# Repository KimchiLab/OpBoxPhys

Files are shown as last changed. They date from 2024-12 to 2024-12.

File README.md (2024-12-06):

# OpBox System for Physiology & Camera Recordings

Physiology acquisition (EEG & EMG) using the **OpBox System**  
(Open Source/Operant Boxes for Behavioral Neurophysiology)
 
Reproducible in vivo electrophysiology experiments require the collection of data from multiple subjects, often for extended periods. Studying multiple subjects for extended periods can be made more efficient through simultaneous recordings, but scaling up recordings to accommodate larger numbers of subjects simultaneously requires coordination and consideration of costs and flexibility. To facilitate this process, we have developed OpBox, an open source set of tools to acquire electroencephalography (EEG) and electromyography (EMG) flexibly from multiple rodent subjects simultaneously. OpBox combines open source hardware and software with off-the-shelf components to create a system that is inexpensive on a per-subject basis and can be easily deployed for multiple subjects. Coded in MATLAB, software widely used in neuroscience laboratories, OpBox scripts can simultaneously collect and display real-time EEG and EMG, and can be integrated with other data streams such as behavior. OpBox also calculates and displays real-time spectral representations and event-related potentials (ERPs). To verify the performance of our system, we compare our amplifiers with two other commercial amplifiers using common benchmarks. We also demonstrate that our acquisition system can reliably record multi-channel data from multiple subjects, and has been successfully tested with at least 12 subjects running simultaneously on a single standard desktop computer. Together, OpBox increases the flexibility and lowers the cost for simultaneous acquisition of electrophysiology data from multiple subjects.

## Folders
* **Amplifier PCB Designs**: Multi-channel, open source OpBox amplifier PCB designs (3 and 4 channel)
* **How to Build and Parts List**: How to build information and parts lists for OpBox amplifiers
* **OpBox Phys Scripts**: MATLAB based scripts to acquire data from OpBox amplifiers, using National Instruments data acquisition devices

## Changing Windows USB Webcam names
* Note, this requires editing the Registry, which should only be undertaken by experienced users at their own risk after backing it up *  
1. Open Device Manager
1. Right click on the camera, select Properties
1. Click on the details tab
1. Under Property, select Driver Key
1. Right click and copy the Value
1. Run regedit.exe
1. Go to HKEY_LOCAL_MACHINE -> SYSTEM -> ControlSet001 (left click on that)
1. Ctrl-F to find: paste the Driver Key Value
1. It should take you to a folder within Enum -> USB
1. Double Click on Friendly Name and adjust the name (e.g. HD USB Camera -> HD USB Camera 01)
1. Back to Device Manager, under Property, select Device instance path
1. Right click and copy the Value
1. Back to Registry Editor
1. Go to HKEY_LOCAL_MACHINE -> SYSTEM -> CurrentControlSet
1. Ctrl-F to find: paste the Device instanc path Value
1. It should take you to a folder within Control -> DeviceClasses
1. Go within that folder to #GLOBAL -> Device Parameters
1. Double Click on Friendly Name and adjust the name (e.g. HD USB Camera -> HD USB Camera 01)
1. Back to Device Manager -> Action -> Scan for Hardware Changes
1. You may need to restart Matlab or at least run imaqreset, which will cause problems if OpBox is running, so stop all recordings first

## FYI: Pinnacle 2 EEG/ 1 EMG Connections

| Mouse Connection | Pinnacle Connector | Pinnacle Label | Plastics1 Cable Color | Plug Pos | Commutator Socket Pos | Commutator color | Amp Channel | BNC Channel | Matlab Color | Desc |
| --- | --- | --- | --- | --- | --- | --- | --- | --- | --- | --- |
| EEG Ant Left | Ant Left | AGND | Red | 4 | 6 | ***Black*** | G | | | |
| EEG Ant Right | Ant Mid | EEG2 | White | 5 | 5 | White | EEG B | 2 | Orange | Contra-A/P|
| EMG Right | Ant Right | EMG B | Black | 6 | 4 | ***Red*** | EMG | | | |
| EEG Post Left | Post Left | EEG Common | Green | 1 | 1 | Green | EEG Ref | | | |
| EEG Post Right | Post Mid | EEG1 | Blue | 2 | 2 | Blue | EEG A | 1 | Blue | Contra-Horiz |
| EMG Left | Post Right | EMG A | Yellow | 3 | 3 | Yellow | EMG | 3 | Yellow | EMG |

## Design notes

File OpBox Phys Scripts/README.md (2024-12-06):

# OpBox Phys

Physiology acquisition (EEG & EMG) using the **OpBox System**  
(Open Source/Operant Boxes for Behavioral Neurophysiology)
 
The OpBox Phys software library was written in MATLAB to use National Instruments Data Acquisition Devices to collect physiology and behavioral data from multiple subjects simultaneously. It requires MATLAB's Data Acquisition Toolbox (R2020a or newer) and NI's DAQmx drivers.

## Scripts/Functions
OpBox MATLAB scripts are grouped into several types:  

* OpBox_\*.m: Intended to be called by users  
* OpBoxPhys_\*.m: Called internally by other scripts
* \*.csv: Spreadsheets (in text based comma separated value format) used for configuration by users

## Main Functions
* *OpBox_Setup*: Setup data acquisition devices
* *OpBox_Add*: Add subjects once the system has been setup
* *OpBox_Remove*: Remove one or more subjects that are currently being recorded from
* *OpBox_Stop*: Stop data acquisition

## Additional functions
* *OpBox\_Axis\_Time*: Change the axis for the display of temporal data
* *OpBox_ResetEP*: Reset the evoked potentials being displayed
* *OpBox_LoadPhysData*: Load data collected in a prior session
	* data = OpBox_LoadPhysData(fullfile(server_dir_name, filename_bin)); % where filename_bin = the name of a binary .bin opbox file

## Configuration
The .csv spreadsheets can be edited using a text editor or standard spreadsheet program. If using a program such as Excel, make sure to save in the same text based .csv format when done

* *InfoBoxes.csv*: Configuration for various the various "OpBoxes". This includes assignments of different DAQ devices and input channels (analog, digital, rotary encoders) to specific boxes/amplifiers. It is also possible to associate webcams.
* *InfoSubjects.csv*: Configuration for assigments of various subjects to various boxes and groups

Webcams can be used to monitor and save video during acquisition, although MATLAB's image acquisition from webcams can be slower than other more dedicated systems. OpBox will try to connect to webcams using MATLAB's winvideo driver. In general OpBox has been written for Windows, but can be adapted to other OSes.

## Acknowledgements

This library includes the file [csvimport.m](http://uk.mathworks.com/matlabcentral/fileexchange/23573-csvimport) in OpBoxPhys_InfoBoxSubj.m
This file is used to load csv files for OpBox in MATLAB R2013a. 
Subsequent MATLAB releases included the function *readtable.m*

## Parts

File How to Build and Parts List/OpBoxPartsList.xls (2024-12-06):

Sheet: OpBox
Ordering frequency | SystemPart | Equipment | Vendor | Cost | # | Total | VendorPart | MfgPart | Manufacturer | Web | Notes | Cost per OpBox | $269.59 | Possible 1 time expenses | $1560.36
For 10 OpBoxes | Physiology: Acquisition from Amplifier | 10' BNC M-M Patch Cable RG58 Coax 50 ohm | M C M Electronics | 3.7700 | 8 | $30.16 | 24-15626 | 24-15626 | Pro Signal | http://www.mcmelectronics.com/product/24-15626 | Connection from Physiology Amplifier to Acquisition
For 10 OpBoxes | Physiology: Battery Power | Battery Holder 2xaa Snap 150mm Lead | M C M Electronics | 0.4100 | 20 | $8.20 | 28-12561 | 23VB21A | Pro Signal | http://www.mcmelectronics.com/product/PRO-POWER-23VB21A-/28-12561 | Battery Holder (2 AA)
For 10 OpBoxes | Physiology: Amplifier | BUMPER CYLIN 0.312" DIA BLK | Digi-Key | 0.0762 | 144 | $10.97 | SJ5746-0-ND | SJ61A1 | 3M | http://www.digikey.com/product-detail/en/SJ61A1/SJ5746-0-ND/1768456 | Rubber bumper feet for amp
For 10 OpBoxes | Physiology: Cable | Cables: 6 Channel Open ended: Spring: 100cm long | Plastics1 | 32.7000 | 10 | $327.00 | 363-000 W/ SPRING |  |  | http://www.plastics1.com/Gallery-PRC.php?CMD=VIEW | Cables: 6 channels with Spring shielding
For 10 OpBoxes: 4Ch | Physiology: Amplifier 4Ch | CAP CER 0.047UF 50V 5% RADIAL | Digi-Key | 0.4600 | 40 | $18.40 | 445-8327-ND | FK16C0G1H473J | TDK Corporation | http://www.digikey.com/product-detail/en/FK16C0G1H473J/445-8327-ND/2815257 | For 2 pole Active Low pass filter, Gain = 1, F = 200 Hz, Q~0.71
For 10 OpBoxes: 3Ch | Physiology: Amplifier 3Ch | CAP CER 0.047UF 50V 5% RADIAL | Digi-Key | 0.4670 | 30 | $14.01 | 445-8327-ND | FK16C0G1H473J | TDK Corporation | http://www.digikey.com/product-detail/en/FK16C0G1H473J/445-8327-ND/2815257 | For 2 pole Active Low pass filter, Gain = 1, F = 200 Hz, Q~0.71
For 10 OpBoxes: 4Ch | Physiology: Amplifier 4Ch | CAP CER 0.1UF 50V 5% RADIAL | Digi-Key | 0.4001 | 280 | $112.03 | 445-8325-ND | FK16C0G1H104J | TDK Corporation | http://www.digikey.com/product-detail/en/FK16C0G1H104J/445-8325-ND/2815255 | For power inputs & 2 pole Active Low pass filter, Gain = 1, F = 200 Hz, Q~0.71. COG 5%
For 10 OpBoxes: 3Ch | Physiology: Amplifier 3Ch | CAP CER 0.1UF 50V 5% RADIAL | Digi-Key | 0.4000 | 210 | $84.00 | 445-8325-ND | FK16C0G1H104J | TDK Corporation | http://www.digikey.com/product-detail/en/FK16C0G1H104J/445-8325-ND/2815255 | For power inputs & 2 pole Active Low pass filter, Gain = 1, F = 200 Hz, Q~0.71. COG 5%
For 10 OpBoxes: 4Ch | Physiology: Amplifier 4Ch | CAP FILM 1UF 63VDC RADIAL | Digi-Key | 0.3120 | 100 | $31.20 | 495-1119-ND | B32529C105J | EPCOS Inc | http://www.digikey.com/product-detail/en/B32529C105J/495-1119-ND/592697 | For 2 pole Active High pass filter, Gain = 1, F = 0.28 Hz, Q~0.71. Film Cap
For 10 OpBoxes: 3Ch | Physiology: Amplifier 3Ch | CAP FILM 1UF 63VDC RADIAL | Digi-Key | 0.4550 | 60 | $27.30 | 495-1119-ND | B32529C105J | EPCOS Inc | http://www.digikey.com/product-detail/en/B32529C105J/495-1119-ND/592697 | For 2 pole Active High pass filter, Gain = 1, F = 0.28 Hz, Q~0.71. Film Cap
For 10 OpBoxes: 3Ch | Physiology: Amplifier 3Ch | CONN BNC JACK R/A 50 OHM PCB | Digi-Key | 1.7252 | 30 | $51.76 | A97553-ND | 1-1337543-0 | TE Connectivity | http://www.digikey.com/product-detail/en/1-1337543-0/A97553-ND/1755940 | BNC output jacks
For 10 OpBoxes: 3Ch | Physiology: Amplifier 3Ch | CONN HEADER VERT .100 2POS 30AU | Digi-Key | 0.7300 | 20 | $14.60 | A28473-ND | 103908-1 | TE Connectivity | http://www.digikey.com/product-detail/en/103908-1/A28473-ND/298654 | AmpModu 2 pin male pins w/housing for amp power input, with Latch. Press-Fit, Solder
For 10 OpBoxes: 4Ch | Physiology: Amplifier 4Ch | CONN HEADER VERT .100 2POS 30AU | Digi-Key | 0.6610 | 20 | $13.22 | A28473-ND | 103908-1 | TE Connectivity | http://www.digikey.com/product-detail/en/103908-1/A28473-ND/298654 | AmpModu 2 pin male pins w/housing for amp power input, with Latch. Press-Fit, Solder
For 10 OpBoxes: 4Ch | Physiology: Amplifier 4Ch | CONN MOD JACK 8P8C | Digi-Key | 4.7690 | 10 | $47.69 | 380-1100-ND | SS-82000-002 |  | http://www.digikey.com/product-detail/en/SS-82000-002/380-1100-ND/459026 | "Ethernet" Input for NI system
For 10 OpBoxes: 4Ch | Physiology: Amplifier 4Ch | CONN MOD JACK R/A 8P8C SHIELDED | Digi-Key | 1.6240 | 10 | $16.24 | 380-1047-ND | SS-7188S-A-NF | Stewart Connector | http://www.digikey.com/product-detail/en/SS-7188S-A-NF/380-1047-ND/388309 | "Ethernet" Output for Amp 4Ch
For 10 OpBoxes | Physiology: Commutator | CONN PIN CONT 26-30AWG GOLD | Digi-Key | 0.0948 | 60 | $5.69 | 1-794613-1-ND | 1-794613-1 | TE Connectivity | http://www.digikey.com/product-detail/en/1-794613-1/1-794613-1-ND/2259374 | Commutator male pins: Mico MATE-N-LOCK, AMP. Male pin contacts. 3mm TE connectors
For 10 OpBoxes | Physiology: Commutator | CONN PLUG 3MM 6POS DL MATE-N-LOK | Digi-Key | 0.6090 | 10 | $6.09 | A30271-ND | 794616-6 | TE Connectivity | http://www.digikey.com/product-detail/en/794616-6/A30271-ND/684994 | Commutator plug: Mico MATE-N-LOCK, AMP. Male pin holder. 3mm TE connectors
For 10 OpBoxes | Physiology: Cable | CONN RCPT 3MM 6POS DL MATE-N-L | Digi-Key | 0.4900 | 10 | $4.90 | A30295-ND | 794617-6 | TE Connectivity | http://www.digikey.com/product-detail/en/794617-6/A30295-ND/685018 | Crimp connectors for male/female pin combo for commutator: Mico MATE-N-LOCK, AMP. Female socket holder
For 10 OpBoxes | Physiology: Battery Power | CONN RECPT 2POS .1" POL UNLOAD | Digi-Key | 0.3570 | 20 | $7.14 | A28393-ND | 104257-1 | TE Connectivity | http://www.digikey.com/product-detail/en/104257-1/A28393-ND/289301 | AmpModu 2 pin housing for female sockets for battery power output, with Latch
For 10 OpBoxes | Physiology: Battery Power | CONN SOCKET 22-26AWG 30AU CRIMP | Digi-Key | 0.1776 | 40 | $7.10 | A32513-ND | 1-104480-6 | TE Connectivity | http://www.digikey.com/product-detail/en/1-104480-6/A32513-ND/1014904 | AmpModu Socket contacts for 2 pin housing at 0.100 spacing for battery power connectors: 22-26 AWG
For 10 OpBoxes | Physiology: Cable | CONN SOCKET 30-26AWG GOLD CRIMP | Digi-Key | 0.1186 | 60 | $7.12 | 1-794611-1-ND | 1-794611-1 | TE Connectivity | http://www.digikey.com/product-detail/en/1-794611-1/1-794611-1-ND/2259415 | Crimp connectors for male/female pin combo for commutator: Mico MATE-N-LOCK, AMP. Female socket contacts. 3mm TE connectors
For 10 OpBoxes: 3Ch | Physiology: Amplifier 3Ch | CONN TERM BLOCK 6POS 5.08MM PCB | Digi-Key | 2.6290 | 10 | $26.29 | 277-1251-ND | 1729160 | Phoenix Contact | http://www.digikey.com/product-detail/en/1729160/277-1251-ND/260619 | Screw Terminal for 6 Ch 0.200" spacing for amp Ch3
For 10 OpBoxes: 4Ch | Physiology: Amplifier 4Ch | CONN TERM BLOCK 6POS 5.08MM PCB | Digi-Key | 3.0260 | 10 | $30.26 | 277-1251-ND | 1729160 | Phoenix Contact | http://www.digikey.com/product-detail/en/1729160/277-1251-ND/260619 | Screw Terminal for 6 Ch 0.200" spacing for amp input
For 10 OpBoxes: 3Ch | Physiology: Amplifier 3Ch | DeliriumLab Amp Printed Circuit Board | Sunstone | 33.8000 | 10 | $338.00 | Custom | OperantShield | DeliriumLab.org | http://deliriumlab.org/ | Custom PCB for Electrophysiology Amplifier
For 10 OpBoxes: 4Ch | Physiology: Amplifier 4Ch | DeliriumLab Amp Printed Circuit Board | Sunstone | 33.8000 | 10 | $338.00 | Custom | OperantShield | DeliriumLab.org | http://deliriumlab.org/ | Custom PCB for Electrophysiology Amplifier
Possible 1 time expense | Computer | Desktop Computer | Dell | 699.9900 | 1 | $699.99 | XPS 8700 |  |  | http://www.dell.com/us/p/xps-8700/pd | Starts at 699.99, previously recommended at least Win7 64 bit, >=8GB RAM, >=1 TB hard disk
Possible 1 time expense | Software | Fritzing |  | 0.0000 | 1 | $0.00 |  |  |  | http://fritzing.org/download/ | For editing printed circuit board
For 10 OpBoxes: 4Ch | Physiology: Amplifier 4Ch | IC OPAMP GP 2.2MHZ 8DIP | Digi-Key | 4.0500 | 80 | $324.00 | 296-7365-5-ND | TLC277IP | Texas Instruments | http://www.digikey.com/product-detail/en/TLC277IP/296-7365-5-ND/374913 | OpAmp (used in OpenEEG too)
For 10 OpBoxes: 3Ch | Physiology: Amplifier 3Ch | IC OPAMP GP 2.2MHZ 8DIP | Digi-Key | 2.1500 | 60 | $129.00 | 296-7365-5-ND | TLC277IP | Texas Instruments | http://www.digikey.com/product-detail/en/TLC277IP/296-7365-5-ND/374913 | OpAmp (used in OpenEEG too)
For 10 OpBoxes: 4Ch | Physiology: Amplifier 4Ch | IC SOCKET STRAIGHT 8POS TIN | Digi-Key | 0.1196 | 120 | $14.35 | AE9986-ND | A08-LC-TT-R | Assman WSW Components | http://www.digikey.com/product-detail/en/A08-LC-TT-R/AE9986-ND/821740 | Chipsets for Amplifiers Integrated Circuits
For 10 OpBoxes: 3Ch | Physiology: Amplifier 3Ch | IC SOCKET STRAIGHT 8POS TIN | Digi-Key | 0.1288 | 90 | $11.59 | AE9986-ND | A08-LC-TT-R | Assman WSW Components | http://www.digikey.com/product-detail/en/A08-LC-TT-R/AE9986-ND/821740 | Chipsets for Amplifiers Integrated Circuits
For 10 OpBoxes: 4Ch | Physiology: Amplifier 4Ch | INA114BP IC OPAMP INSTR 1MHZ 8DIP | Digi-Key | 11.8364 | 40 | $473.46 | INA114BP-ND | INA114BP | Texas Instruments | http://www.digikey.com/product-search/en?pv975=10&FV=1140050&k=ina114&mnonly=0&newproducts=0&ColumnSort=0&page=1&stock=1&quantity=0&ptm=0&fid=0&pageSize=500 | Instrument Amp (used in OpenEEG too)
For 10 OpBoxes: 3Ch | Physiology: Amplifier 3Ch | INA114BP IC OPAMP INSTR 1MHZ 8DIP | Digi-Key | 12.1044 | 30 | $363.13 | INA114BP-ND | INA114BP | Texas Instruments | http://www.digikey.com/product-search/en?pv975=10&FV=1140050&k=ina114&mnonly=0&newproducts=0&ColumnSort=0&page=1&stock=1&quantity=0&ptm=0&fid=0&pageSize=500 | Instrument Amp (used in OpenEEG too)
For 10 OpBoxes | Physiology: Amplifier | LED 3MM HI EFF RED RED DIFF | Digi-Key | 0.3220 | 20 | $6.44 | 160-1957-ND | LTL-4221NLC | Lite-On Inc | http://www.digikey.com/product-detail/en/LTL-4221NLC/160-1957-ND/3198526 | LED Indicators for Amp Power
Possible 1 time expense | Software | Matlab: Data Acquisition Toolbox |  | 200.0000 | 1 | $200.00 |  |  |  | http://www.mathworks.com/ | Maltab Perpetual Academic Pricing. Student & Personal pricing are lower if applicable
Possible 1 time expense | Software | Matlab: IDE |  | 500.0000 | 1 | $500.00 |  |  |  | http://www.mathworks.com/ | Maltab Perpetual Academic Pricing. Student & Personal pricing are lower if applicable. Recommend R2013a or more recent for continuous clocked digital & analog data acquisition
For 10 OpBoxes | Physiology: Battery Power | MEDC BATTERIES ALK AA 1.5 VOLT BX/24EA | Owens & Minor | 3.8100 | 2 | $7.62 | 1314BATTAA | BATTAA | OM MAIN STREET | http://www.owens-minor.com/Pages/default.aspx | Batteries: AA Alkaline
For 10 OpBoxes | Physiology: Acquisition from Amplifier | NI CB-68LPR Unshielded 68-pin I/O Connector Block | National Instruments | 114.0000 | 2 | $228.00 | 777145-02 |  |  | http://sine.ni.com/nips/cds/view/p/lang/en/nid/1186 | Breakout board for NI PCI cards
For 10 OpBoxes | Physiology: Acquisition from Amplifier | NI PCI-6225 16-Bit, 250 kS/s, 80 Analog Inputs Multifunction DAQ | National Instruments | 1348.0000 | 1 | $1348.00 | 779295-01 |  |  | http://sine.ni.com/nips/cds/view/p/lang/en/nid/201605 | Acquisition Card: 40 Differential Analog Inputs, 8 Clocked Digital Inputs
For 10 OpBoxes | Physiology: Acquisition from Amplifier | NI PCIe-6323 X Series Data Acquisition | National Instruments | 869.0000 | 0 | $0.00 | 781045-01 |  |  | http://sine.ni.com/nips/cds/view/p/lang/en/nid/207406 | Acquisition Card: 16 Differential Analog Inputs, 32 Clocked Digital Inputs. If subsitute or add this to PCI-6225, will have to substitute shielded cables since analog & digital are mixed on both boxes and double the overall number of NI parts (16 channels = 5 subjects)
For 10 OpBoxes | Physiology: Acquisition from Amplifier | NI SHC68-68 Cable (2m) | National Instruments | 103.0000 | 1 | $103.00 | 191945-02 |  |  | http://sine.ni.com/nips/cds/view/p/lang/en/nid/201629 | No shielding for analog only portion of PCI-6225, Recommended by NI
For 10 OpBoxes | Physiology: Acquisition from Amplifier | NI SHC68-68-EPM Cable (2m) | National Instruments | 140.0000 | 1 | $140.00 | 192061-02 |  |  | http://sine.ni.com/nips/cds/view/p/lang/en/nid/201628 | Shielded cable for shared analog & digital portion
For 10 OpBoxes | Physiology: Acquisition from Amplifier | NI USB-6009 14-Bit, 48 kS/s Low-Cost Multifunction DAQ | National Instruments | 299.0000 | 1 | $299.00 | 779026-01 |  |  | http://sine.ni.com/nips/cds/view/p/lang/en/nid/201987 | Acquisition Device: USB: 4 Differential Analog Inputs, but no clocked Digital Inputs. If use this do not need breakout boards and cables, but will need 10, 1 for each subject. The behavioral data will then need to be multiplexed into the remaining analog channel
Possible 1 time expense | Software | OpBox Scripts |  | 0.0000 | 1 | $0.00 |  |  |  | http://deliriumlab.org/ | For OpBoxPhys Matlab scripts
For 10 OpBoxes: 4Ch | Physiology: Amplifier 4Ch | RES 100K OHM 1/4W 0.1% AXIAL | Digi-Key | 0.3326 | 80 | $26.61 | 100KADCT-ND | MFP-25BRD52-100K | Yageo | http://www.digikey.com/product-detail/en/MFP-25BRD52-100K/100KADCT-ND/2059112 | For bias currents at inputs
For 10 OpBoxes: 3Ch | Physiology: Amplifier 3Ch | RES 100K OHM 1/4W 0.1% AXIAL | Digi-Key | 0.1497 | 60 | $8.98 | 100KADCT-ND | MFP-25BRD52-100K | Yageo | http://www.digikey.com/product-detail/en/MFP-25BRD52-100K/100KADCT-ND/2059112 | For bias currents at inputs
For 10 OpBoxes: 4Ch | Physiology: Amplifier 4Ch | RES 100K OHM 1/4W 1% AXIAL | Digi-Key | 0.0311 | 100 | $3.11 | 100KXBK-ND | MFR-25FBF52-100K | Yageo | http://www.digikey.com/product-detail/en/MFR-25FBF52-100K/100KXBK-ND/13473 | For 10x Gain across Op Amp
For 10 OpBoxes: 3Ch | Physiology: Amplifier 3Ch | RES 100K OHM 1/4W 1% AXIAL | Digi-Key | 0.0580 | 60 | $3.48 | 100KXBK-ND | MFR-25FBF52-100K | Yageo | http://www.digikey.com/product-detail/en/MFR-25FBF52-100K/100KXBK-ND/13473 | For 10x Gain across Op Amp
For 10 OpBoxes: 4Ch | Physiology: Amplifier 4Ch | RES 10K OHM 1/4W 1% AXIAL | Digi-Key | 0.3150 | 100 | $31.50 | 10.0KXBK-ND | MFR-25FBF52-10K | Yageo | http://www.digikey.com/product-detail/en/MFR-25FBF52-10K/10.0KXBK-ND/13219 | For 10x Gain across Op Amp
For 10 OpBoxes: 3Ch | Physiology: Amplifier 3Ch | RES 10K OHM 1/4W 1% AXIAL | Digi-Key | 0.0580 | 60 | $3.48 | 10.0KXBK-ND | MFR-25FBF52-10K | Yageo | http://www.digikey.com/product-detail/en/MFR-25FBF52-10K/10.0KXBK-ND/13219 | For 10x Gain across Op Amp
For 10 OpBoxes: 4Ch | Physiology: Amplifier 4Ch | RES 15K OHM 1/4W 1% AXIAL | Digi-Key | 0.0436 | 50 | $2.18 | 15.0KXBK-ND | MFR-25FBF52-15K | Yageo | http://www.digikey.com/product-detail/en/MFR-25FBF52-15K/15.0KXBK-ND/13252 | For 2 pole Active Low pass filter, Gain = 1, F = 200 Hz, Q~0.71
For 10 OpBoxes: 3Ch | Physiology: Amplifier 3Ch | RES 15K OHM 1/4W 1% AXIAL | Digi-Key | 0.0580 | 30 | $1.74 | 15.0KXBK-ND | MFR-25FBF52-15K | Yageo | http://www.digikey.com/product-detail/en/MFR-25FBF52-15K/15.0KXBK-ND/13252 | For 2 pole Active Low pass filter, Gain = 1, F = 200 Hz, Q~0.71
For 10 OpBoxes: 4Ch | Physiology: Amplifier 4Ch | RES 1M OHM 1/4W 1% AXIAL | Digi-Key | 0.0436 | 50 | $2.18 | 1.00MXBK-ND | MFR-25FBF52-1M | Yageo | http://www.digikey.com/product-detail/en/MFR-25FBF52-1M/1.00MXBK-ND/13714 | For 2 pole Active High pass filter, Gain = 1, F = 0.28 Hz, Q~0.71
For 10 OpBoxes: 3Ch | Physiology: Amplifier 3Ch | RES 1M OHM 1/4W 1% AXIAL | Digi-Key | 0.0580 | 30 | $1.74 | 1.00MXBK-ND | MFR-25FBF52-1M | Yageo | http://www.digikey.com/product-detail/en/MFR-25FBF52-1M/1.00MXBK-ND/13714 | For 2 pole Active High pass filter, Gain = 1, F = 0.28 Hz, Q~0.71
For 10 OpBoxes: 4Ch | Physiology: Amplifier 4Ch | RES 499K OHM 1/4W 1% AXIAL | Digi-Key | 0.0436 | 50 | $2.18 | 499KXBK-ND | MFR-25FBF52-499K | Yageo | http://www.digikey.com/product-detail/en/MFR-25FBF52-499K/499KXBK-ND/13656 | For 2 pole Active High pass filter, Gain = 1, F = 0.28 Hz, Q~0.71
For 10 OpBoxes: 3Ch | Physiology: Amplifier 3Ch | RES 499K OHM 1/4W 1% AXIAL | Digi-Key | 0.0580 | 30 | $1.74 | 499KXBK-ND | MFR-25FBF52-499K | Yageo | http://www.digikey.com/product-detail/en/MFR-25FBF52-499K/499KXBK-ND/13656 | For 2 pole Active High pass filter, Gain = 1, F = 0.28 Hz, Q~0.71
For 10 OpBoxes: 4Ch | Physiology: Amplifier 4Ch | RES 5.62K OHM 1/4W 1% AXIAL | Digi-Key | 0.0442 | 60 | $2.65 | 5.62KXBK-ND | MFR-25FBF52-5K62 | Yageo | http://www.digikey.com/product-detail/en/MFR-25FBF52-5K62/5.62KXBK-ND/13171 | Across Instrument Amplifier for Gain of 10x (1+50/5.62) & For LED Indicators
For 10 OpBoxes: 3Ch | Physiology: Amplifier 3Ch | RES 5.62K OHM 1/4W 1% AXIAL | Digi-Key | 0.0580 | 50 | $2.90 | 5.62KXBK-ND | MFR-25FBF52-5K62 | Yageo | http://www.digikey.com/product-detail/en/MFR-25FBF52-5K62/5.62KXBK-ND/13171 | Across Instrument Amplifier for Gain of 10x (1+50/5.62) & For LED Indicators
For 10 OpBoxes: 4Ch | Physiology: Amplifier 4Ch | RES 9.09K OHM 1/4W 1% AXIAL | Digi-Key | 0.0436 | 50 | $2.18 | 9.09KXBK-ND | MFR-25FBF52-9K09 | Yageo | http://www.digikey.com/product-detail/en/MFR-25FBF52-9K09/9.09KXBK-ND/13211 | For 2 pole Active Low pass filter, Gain = 1, F = 200 Hz, Q~0.71
For 10 OpBoxes: 3Ch | Physiology: Amplifier 3Ch | RES 9.09K OHM 1/4W 1% AXIAL | Digi-Key | 0.0580 | 30 | $1.74 | 9.09KXBK-ND | MFR-25FBF52-9K09 | Yageo | http://www.digikey.com/product-detail/en/MFR-25FBF52-9K09/9.09KXBK-ND/13211 | For 2 pole Active Low pass filter, Gain = 1, F = 200 Hz, Q~0.71
For 10 OpBoxes | Physiology: Commutator | Slip Ringer with Flange | Adafruit | 14.9500 | 10 | $149.50 | 736 | 736 | Adafruit Industries | https://www.adafruit.com/product/736 | Commutator: 6 channels
Possible 1 time expense | Solder | Solder with Rosin Flux Core for Electronics 0.031" Diameter, 370°F Melting Temperature, 1 lb. without Silver | McMaster | 33.3700 | 1 | $33.37 | 7659A5 |  |  | http://www.mcmaster.com/#7659a5/=ugau56 | Standard solder for electronics
Possible 1 time expense | Solder | Soldering Stations > WES51 | DigiKey | 127.0000 | 1 | $127.00 | WES51-120V-ND |  |  | http://www.digikey.com/product-detail/en/WES51/WES51-120V-ND/526397 | Standard soldering station
For 10 OpBoxes: 3Ch | Physiology: Amplifier 3Ch | Switch PCB Dpdt Horiz | M C M Electronics | 2.0200 | 10 | $20.20 | 26-4370 | 98K4951 | Multicomp | http://www.mcmelectronics.com/product/MULTICOMP-98K4951-/26-4370 | Switch for Amplifier power
For 10 OpBoxes: 4Ch | Physiology: Amplifier 4Ch | Toggle Switch, On-Off-On, SPDT | Newark | 2.1600 | 10 | $21.60 | 98K4978 | 1MS3T2B4M7RE | Multicomp | https://www.newark.com/multicomp/1ms3t2b4m7re/switch-toggle-spdt-100ma-20v/dp/98K4978 | Switch for Amplifier power

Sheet: HomeCage
Ordering freq | SystemPart | Equipment | Vendor | Cost | #Total | #Have | #Need | Total | VendorPart | MfgPart | Manufacturer | Web | Notes | Cost per OpBox | $0.00 | Possible 1 time expenses | $0.00
For 8 OpBoxes | HomeCage | Home cage bottom | CCM |  | 8 | 8 | 0 | $0.00
For 8 OpBoxes | HomeCage | Home cage top | CCM |  | 8 | 8 | 0 | $0.00 |  |  |  |  | Remove top grating, cut filter to thirds
For 8 OpBoxes | HomeCage | Home cage grid insert | 3d Print |  | 16 | 16 | 0 | $0.00
For 8 OpBoxes | HomeCage | Home cage central insert | 3d Print |  | 8 | 8 | 0 | $0.00
For 8 OpBoxes | HomeCage | Camus Food Hopper Bottom | 3d Print |  | 16 | 0 | 16 | $0.00 |  |  |  |  | Print more food hoppers
For 8 OpBoxes | HomeCage | Camus Food Hopper Extended Top | 3d Print |  | 8 | 8 | 0 | $0.00
For 8 OpBoxes | HomeCage | Camus Water Bottle | AliExpress |  | 8 | 8 | 0 | $0.00
For 8 OpBoxes | HomeCage | Camus Water Bottle Holder Bottom | 3d Print |  | 16 | 0 | 16 | $0.00 |  |  |  |  | Need to redesign?
For 8 OpBoxes | HomeCage | Camus Water Bottle Holder Extended Top | 3d Print |  | 8 | 0 | 8 | $0.00 |  |  |  |  | Need to redesign?
For 8 OpBoxes | HomeCage | Bedding | 3d Print |  | 8 | 8 | 0 | $0.00
For 8 OpBoxes | HomeCage | Nestlet | 3d Print |  | 8 | 8 | 0 | $0.00
For 8 OpBoxes | HomeCage | Filters cut to thirds (only using outer 3rds) | 3d Print |  | 16 | 16 | 0 | $0.00
For 8 OpBoxes | Camera | Camera Housing | 3d Print |  | 8 | 8 | 0 | $0.00
For 8 OpBoxes | Camera | Webcam | ELP |  | 8 | 8 | 0 | $0.00
For 8 OpBoxes | Camera | Webcam Lens 2.1mm 5MP 1/2.5" IR | Amazon |  | 8 | 8 | 0 | $0.00 |  |  |  |  | Confirm that have 8
For 8 OpBoxes | Camera | IR LED board | Spinel |  | 8 | 8 | 0 | $0.00 |  |  |  |  | Remove photosensor
For 8 OpBoxes | Camera | USB2 A to A Extension Cord (1m) |  |  | 4 | 4 | 0 | $0.00 |  |  |  |  | Closer cameras
For 8 OpBoxes | Camera | USB2 A to A Extension Cord (2m) |  |  | 4 | 4 | 0 | $0.00 |  |  |  |  | Further cameras
For 8 OpBoxes | Camera | Cover for USB2 A to A Extension Cord (1m) | 3d Print |  | 4 | 4 | 0 | $0.00 |  |  |  |  | Closer cameras
For 8 OpBoxes | Camera | Cover for USB2 A to A Extension Cord (2m) | 3d Print |  | 4 | 4 | 0 | $0.00 |  |  |  |  | Further cameras
For 8 OpBoxes | Computer | 4 Port USB 3.0 PCIe Card w/ 4 Dedicated 5Gbps Channels (USB 3.2 Gen 1) - UASP - SATA / LP4 Power - PCI Express Adapter Card | Amazon | $75.56 | 2 | 2 | 0 | $151.12 | B00HJZEA2S | PEXUSB3S44V | StarTech | https://www.amazon.com/StarTech-com-Express-SuperSpeed-Dedicated-Channels/dp/B00HJZEA2S | Each can do 4 cameras
For 8 OpBoxes | Computer | AMD 7950X3D Computer | Amazon |  | 1 | 1 | 0 | $0.00 |  |  |  |  | Can do 8 amps & cameras
For 8 OpBoxes | Data Acquisition | PCI Express, 32 AI (16-Bit, 250 kS/s), 4 AO (900 kS/s), 48 DIO Multifunction I/O Device | NI | $1248.00 | 2 | 2 | 0 | $2496.00 | PCIe-6323 | PCIe-6323 | NI | https://www.ni.com/en-us/shop/model/pcie-6323.html | Each can do 4 cages
For 8 OpBoxes | Data Acquisition | 68-Pin VHDCI Male to 68-Pin D-SUB Female, Twisted Pair, Shielded Multifunction Cable | NI | $185.00 | 4 | 4 | 0 | $740.00 | SHC68-68-EPM | SHC68-68-EPM | NI | https://www.ni.com/en-us/support/model.shc68-68-epm.html | 2 for each set of 4 cages
For 8 OpBoxes | Data Acquisition | 68-Pin Female VHDCI Right Angle to 68-Pin Female Screw Terminal, Desktop Mount Terminal Block | NI | $190.00 | 4 | 4 | 0 | $760.00 | CB-68LPR | CB-68LPR | NI | https://www.ni.com/en-us/support/model.cb-68lpr.html | 2 for each set of 4 cages
For 8 OpBoxes | Data Acquisition | Connection Box: Amp -> NI | 3d Print |  | 4 | 4 | 0 | $0.00 |  |  |  |  | 2 for each set of 4 cages
For 8 OpBoxes | Amp | Headstage cable (26cm) |  |  | 8 | 0 | 8 | $0.00 |  |  |  |  | Need to cut and solder rectangular male pin connections, but have enough to change/make
For 8 OpBoxes | Amp | Commutator |  |  | 8 | 8 | 0 | $0.00 |  |  |  |  | 6 channels
For 8 OpBoxes | Amp | OpBox Amp (3 channel) |  |  | 8 | 8 | 0 | $0.00
For 8 OpBoxes | Amp | OpBox Amp Housing |  |  | 8 | 8 | 0 | $0.00 |  |  | Hammond |  | Drill screw holes to secure amp (bit size = 5/32" gives extra clearance)
For 8 OpBoxes | Amp | Batteries (4 AA/amp) |  |  | 32 | 32 | 0 | $0.00
For 8 OpBoxes | Amp | BNC Cables |  |  | 24 | 24 | 0 | $0.00
For 8 OpBoxes | Amp | BNC Connections |  |  | 24 | 24 | 0 | $0.00
For 8 OpBoxes | Cables | Thinner Springs |  |  | 8 | 0 | 8 | $0.00 |  |  |  |  | Need to cut and solder rectangular male pin connections, but have enough to change/make
For 8 OpBoxes | Cables | Thin Wires (26cm) |  |  | 48 | 0 | 48 | $0.00
For 8 OpBoxes | Cables | Top Harwin Connectors |  |  | 8 | 0 | 8 | $0.00
For 8 OpBoxes | Cables | Pins |  |  | 48 | 0 | 48 | $0.00

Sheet: CostReport
Sum of Total
Ordering frequency | SystemPart | Total
For 10 OpBoxes | Physiology: Acquisition from Amplifier | $2148.16 | $214.82
 | Physiology: Battery Power | $30.06 | $3.01
 | Physiology: Cable | $339.02 | $33.90
 | Physiology: Commutator | $161.28 | $16.13
 | Physiology: Amplifier | $17.41 | $1.74
For 10 OpBoxes Total |  | $2695.93 | $269.59
Possible 1 time expense | Computer | $699.99 | $70.00
 | Solder | $160.37 | $16.04
 | Software | $700.00 | $70.00
Possible 1 time expense Total |  | $1560.36 | $156.04
For 10 OpBoxes: 3Ch | Physiology: Amplifier 3Ch | $1105.68 | $110.57
For 10 OpBoxes: 3Ch Total |  | $1105.68 | $110.57
For 10 OpBoxes: 4Ch | Physiology: Amplifier 4Ch | $1513.04 | $151.30
For 10 OpBoxes: 4Ch Total |  | $1513.04 | $151.30
Grand Total |  | $6875.01 | $687.50

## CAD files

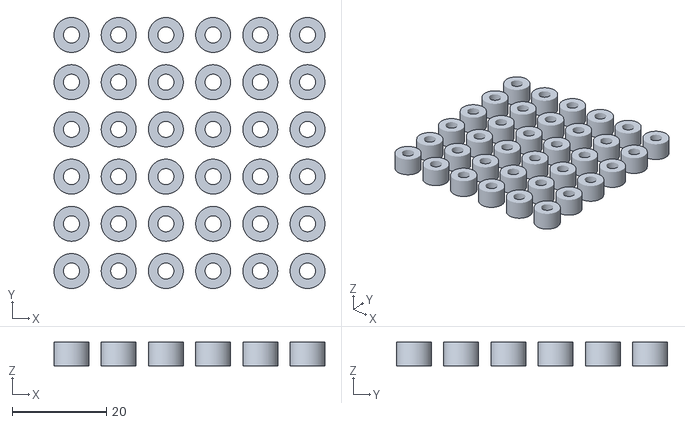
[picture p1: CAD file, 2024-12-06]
3dPrint/AmpStandoff/AmpStandoff.stl
57.4 x 57.4 x 5.00

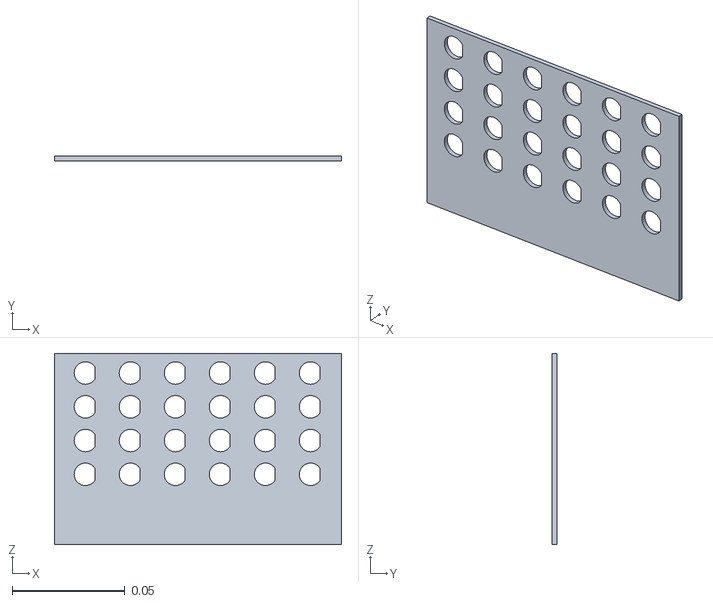
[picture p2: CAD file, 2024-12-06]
3dPrint/BncBreakoutBox/BncBreakoutBox_FrontPanel.stl
0.127 x 0.002 x 0.085

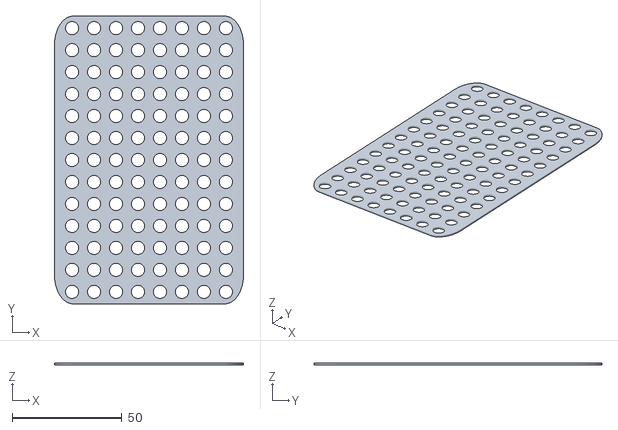
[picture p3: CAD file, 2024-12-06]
3dPrint/CageTopGrid/CageTopGrid.stl
86.0 x 131.0 x 1.00

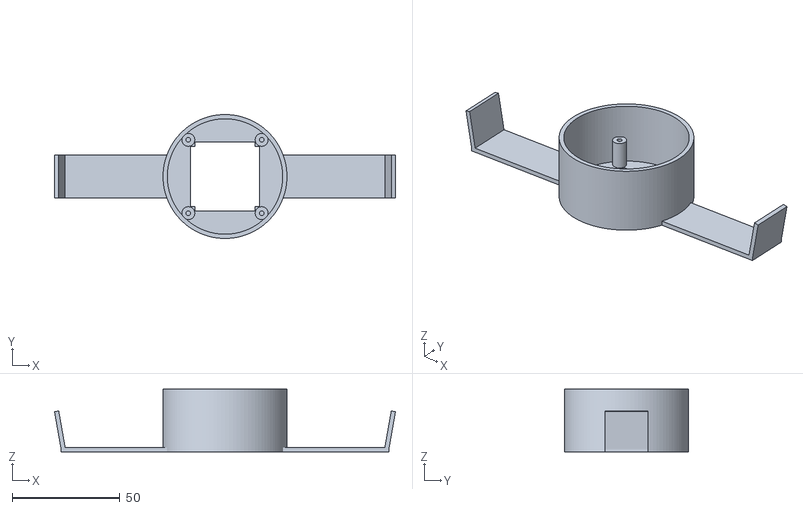
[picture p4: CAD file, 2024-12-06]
3dPrint/CameraHolder/CameraHolderInside.stl
158.1 x 57.5 x 29.0

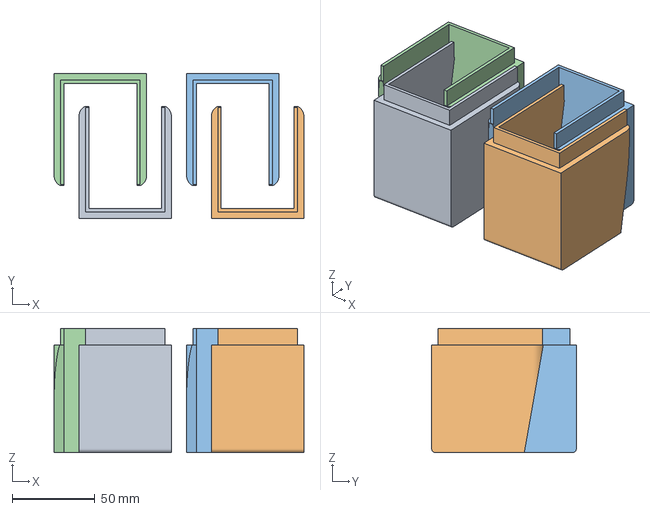
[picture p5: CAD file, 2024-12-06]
3dPrint/FoodHopper/Food Hopper_Cap4.3mf
151.0 x 87.5 x 75.0 mm

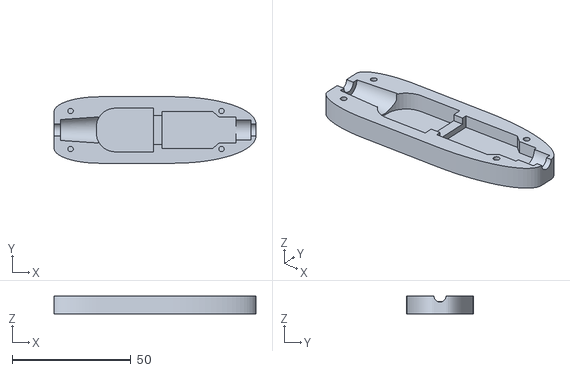
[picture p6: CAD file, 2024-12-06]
3dPrint/UsbCover/CameraHolder_UsbCover_PassiveExt_StarTech_Bottom.stl
85.0 x 28.0 x 7.50

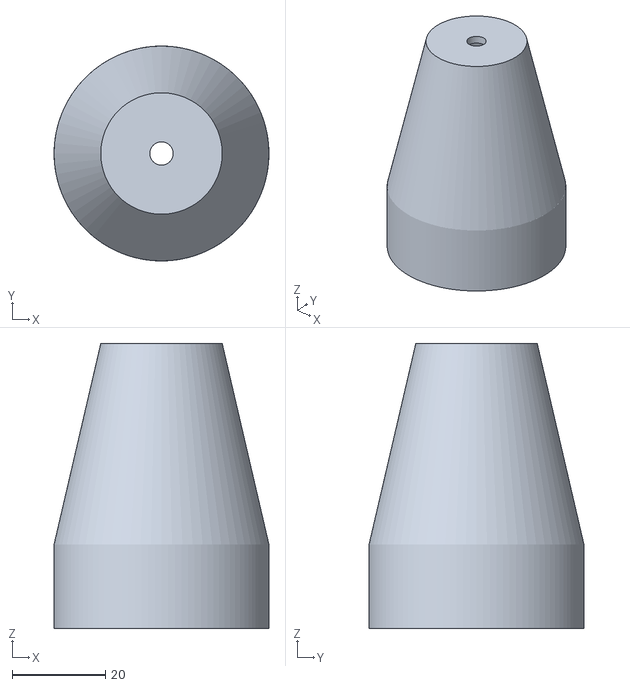
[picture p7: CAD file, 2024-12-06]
3dPrint/WaterBottleHolder/WaterBottleCap.stl
46.0 x 46.0 x 61.0

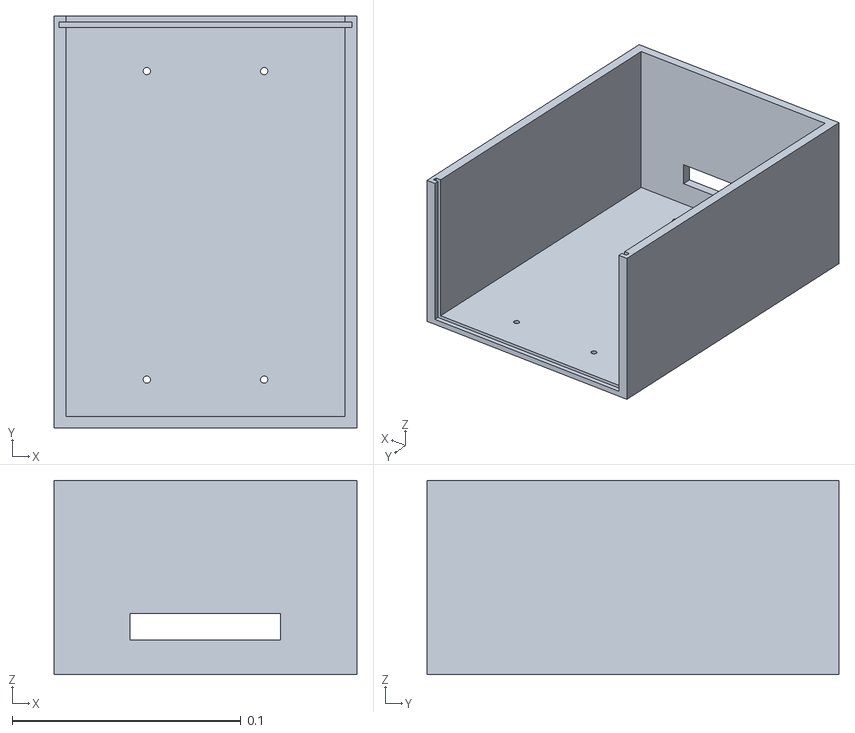
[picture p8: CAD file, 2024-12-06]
3dPrint/BncBreakoutBox/BncBreakoutBox_Box.stl
0.132 x 0.18 x 0.085

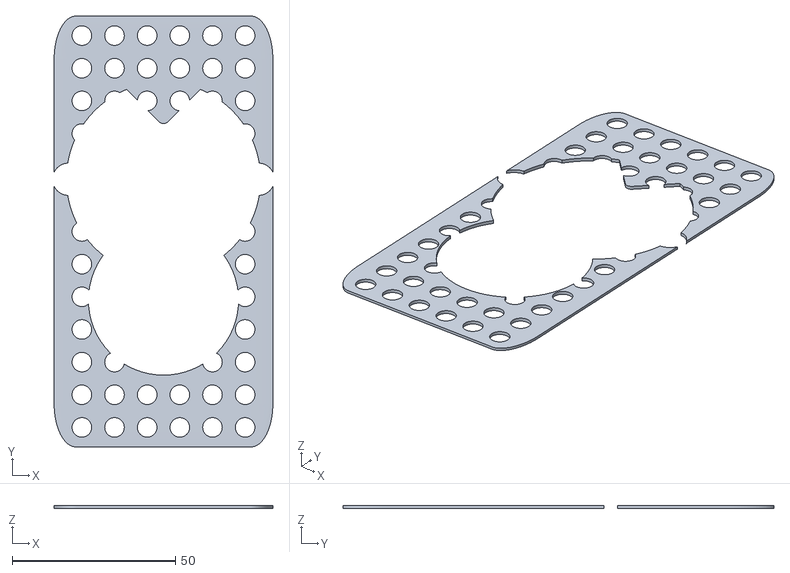
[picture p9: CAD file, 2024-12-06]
3dPrint/CageTopGrid/CageTopGridCenter.stl
67.0 x 132.0 x 1.00

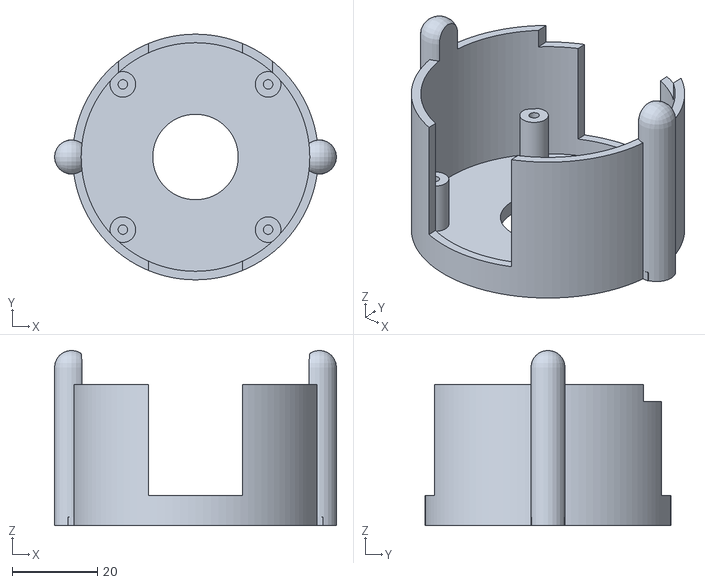
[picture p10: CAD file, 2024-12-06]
3dPrint/CameraHolder/CameraHolderOutside.stl
66.0 x 57.5 x 41.0

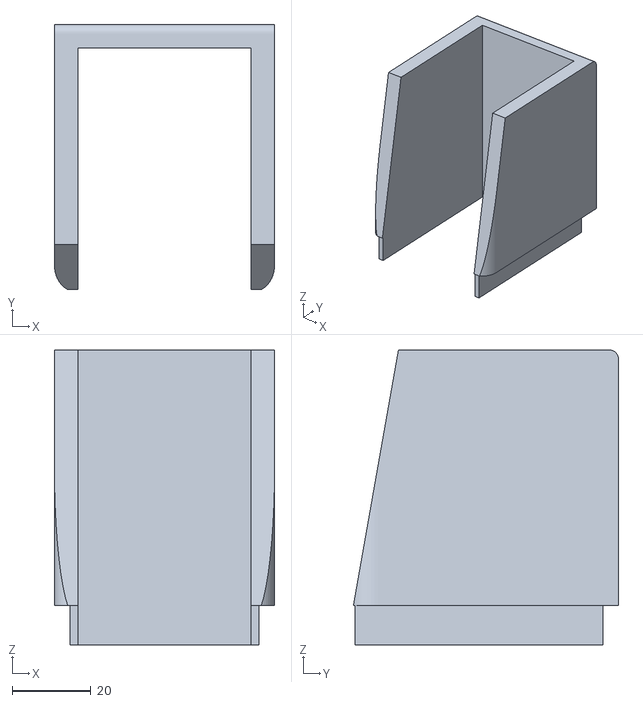
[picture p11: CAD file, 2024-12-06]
3dPrint/FoodHopper/Food Hopper_Cap.stl
56.0 x 67.5 x 75.0

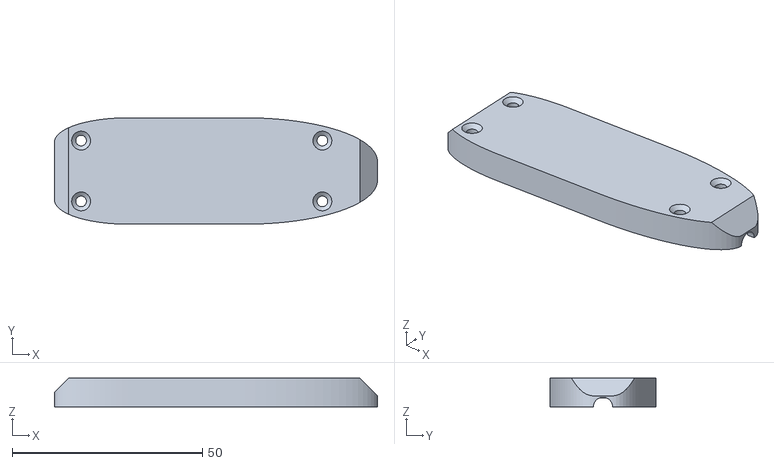
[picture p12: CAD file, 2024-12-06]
3dPrint/UsbCover/CameraHolder_UsbCover_PassiveExt_StarTech_Top.stl
85.0 x 28.0 x 7.50

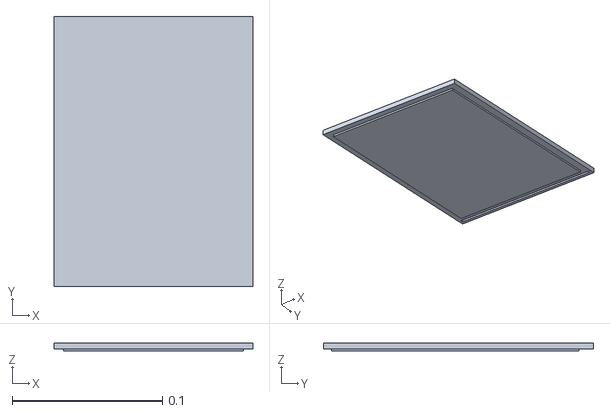
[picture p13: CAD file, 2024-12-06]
3dPrint/BncBreakoutBox/BncBreakoutBox_Top.stl
0.132 x 0.18 x 0.00557

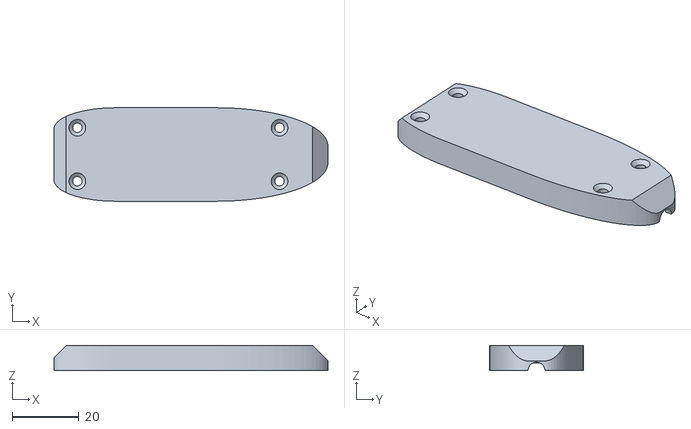
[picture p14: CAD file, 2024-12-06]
3dPrint/UsbCover/CameraHolder_UsbCover_PassiveExt_TrippLite_Top.stl
82.0 x 28.0 x 7.50

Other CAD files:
3dPrint/UsbCover/CameraHolder_UsbCover_PassiveExt_TrippLite_Bottom.stl
3dPrint/UsbCover/CameraHolder_UsbCover_PassiveExt_Array.3mf
3dPrint/CameraHolder/Archive/CameraHolder_LedElp.stl
3dPrint/CameraHolder/Archive/CameraHolder_PhotosensorCap_ELP.stl
3dPrint/CameraHolder/Archive/CameraHolder_CameraCover.stl
3dPrint/CameraHolder/Archive/CameraHolder_FlatLedCap.stl
3dPrint/CameraHolder/Archive/CameraHolder_LedSpinel.stl

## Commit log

2018-10-11 Recopied active files
    [InfoBoxes.csv]
2018-10-11 Removed desktop.ini
    [InfoBoxes1.csv, InfoSubjects1.csv]
2020-05-22 Sub folder organization
    [InfoBoxes.csv, InfoSubjects.csv, OpBoxAmpPartsList.xls]
2020-08-14 OpBox camera synch .ocs files added
    [InfoSubjects.csv]
2024-05-30 Configuration for local boxes and refining video attempts
    [InfoBoxes.csv, InfoSubjects.csv]
2024-07-17 Camera Holder In Cage addition/edits
    [CameraHolder.blend, CameraHolder.stl, CameraHolder_CameraCover.blend, CameraHolder_CameraCover.stl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]
2024-07-18 CameraHolder Inside and Outside
    [CameraHolderInside.blend, CameraHolderInside.stl, CameraHolderOutside.blend]
2024-07-18 CameraHolderOutside Make more compact
    [CameraHolderOutside.blend, CameraHolderOutside.stl]
2024-07-18 CamerHolderInside narrower and higher
    [CameraHolderInside.blend, CameraHolderInside.stl]
2024-07-18 CameraHolderOutside edits
    [CameraHolderOutside.blend, CameraHolderOutside.stl]
2024-07-18 CameraHolderOutside edits, asymmetric
    [CameraHolderOutside.blend, CameraHolderOutside.stl]
2024-07-25 Modifying code for 8 boxes
    [InfoBoxes.csv, InfoSubjects.csv]
2024-07-26 Prelim addition of home cage video parts to PartsList
    [OpBoxAmpPartsList.xls, OpBoxPartsList.xls]
2024-07-26 Amp Standoff shortened to 5mm
    [AmpStandoff.blend, AmpStandoff.stl]
2024-07-27 3d Parts extra initial addition, need to edit parts
    [CameraHolder_UsbCover_ActiveExt_TrippLite.blend, CameraHolder_UsbCover_NonActiveExt_TrippLite.blend, Food Hopper.blend, OpBoxPartsList.xls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]
2024-07-28 Initial USB cover edits
    [CameraHolder_UsbCover_ActiveExt_TrippLite.blend, CameraHolder_UsbCover_NonActiveExt_TrippLite.blend, CameraHolder_UsbCover_PassiveExt_TrippLite.blend, CameraHo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]
2024-07-28 USB Cover StarTech cable mod
    [CameraHolder_UsbCover_PassiveExt_StarTech.blend, CameraHolder_UsbCover_PassiveExt_StarTech_Bottom.stl]
2024-07-28 Early USB Cover Tripp Lite version cover edits
    [CameraHolder_UsbCover_PassiveExt_TrippLite.blend, CameraHolder_UsbCover_PassiveExt_TrippLite_Bottom.stl]
2024-07-28 USB Cover StarTech Early Edits
    [CameraHolder_UsbCover_PassiveExt_StarTech.blend, CameraHolder_UsbCover_PassiveExt_StarTech_Bottom.stl]
2024-07-28 USB Cover Edits
    [CameraHolder_UsbCover_PassiveExt_Array.3mf, CameraHolder_UsbCover_PassiveExt_StarTech.blend, CameraHolder_UsbCover_PassiveExt_StarTech_Bottom.stl, CameraHolder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]
2024-07-29 Extended water bottle cap 25mm higher
    [WaterBottleCap.blend, WaterBottleCap.stl]
2024-07-29 CageTop 3dprint edits
    [CageTopGridCenter.blend, CageTopGridCenter.stl, CameraHolder_PhotosensorCap_Spinel.blend, CameraHolder_PhotosensorCap_Spinel_Array.stl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]
2024-07-30 CageTopGrid changing
    [CageTopGridCenter.blend, CageTopGridCenter.stl]
2024-07-30 3d model edits
    [CageTopGridCenter.blend, CageTopGridCenter.stl, Food Hopper.blend, Food Hopper_Cap.stl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]
2024-07-30 GridTopCenter edit
    [CageTopGridCenter.blend, CageTopGridCenter.stl]
2024-07-30 CageTopGridCenter edits
    [CageTopGridCenter.blend, CageTopGridCenter.stl]
2024-07-31 Added support for camera names, registry instructions
    [InfoBoxes.csv]
2024-08-01 Added more boxes with text
    [InfoBoxes.csv]
2024-08-01 Video code try edits, not done
    [OpBoxPartsList.xls]
2024-08-02 Parallel camera attempts, not yet fixed
2024-08-06 Initial SPMD edits for multiple cameras, not yet working
2024-08-06 Water bottle cap edits
    [FoodHopperAndWaterCap8.3mf, WaterBottleCap.blend, WaterBottleCap.stl]
2024-08-06 Still in process of adding multiple cameras
2024-08-06 Minor edits, vide files not saving completely currently
2024-08-09 Bnc Breakout Box edits
    [BncBreakoutBox.blend, BncBreakoutBox_Box.stl, BncBreakoutBox_FrontPanel.stl, BncBreakoutBox_Top.stl]
2024-08-09 BncBreakoutBox initial commit
    [BncBreakoutBox.blend]
2024-08-09 Subject blank now text, Example Pinnacle pinouts
    [InfoBoxes.csv]
2024-08-30 3d print files
    [Food Hopper_Cap4.3mf]
